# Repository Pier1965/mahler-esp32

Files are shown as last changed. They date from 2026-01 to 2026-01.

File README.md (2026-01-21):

ESP 32 LOGGER FOR MAHLER CALORIMETER
-------------------------------------
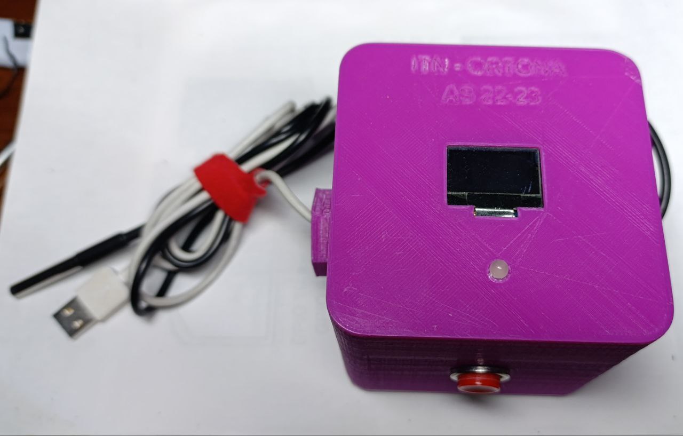
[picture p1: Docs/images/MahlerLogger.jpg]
Mahler temperature logger

CONFIGURAZIONE
---------------
I file da modificare prima della compilazione sono:
1. `include/config/define.h` per compilazione condizionale;
2. `include/config/hw_settings.h` per pin e parametri riguardanti l'hw;
3. `include/config/mail_settings.h` per i parametri SMTP del provider di posta elettronica;
4. `include/config/ntp_settings.h` eventuale cambio del server ntp, ora locale e ora legale;
5. `include/config/parametri_prova.h` contiene il numero massimo di misure da fare e il tempo tra le stesse in millisecondi;
6. `src/globals/global_variables.cpp` la mail del ricevente di default, che può anche essere cambiata
a run time dal portale MahlerAP;

USO
-----
1. Attivare l'ESP32;
    - Se la rete non è configurata, connettersi a "MahlerAP" con un cellulare o altro;
    - Se si vuole cambiare la rete cui si connette ESP, in modalità OZIOSO schiacciare per 10s il pulsante
(led color bianco. e connettersi a "MahlerAP" con un cellulare o altro;
2. Con il browser andare all'indirizzo 192.168.4.1 e immettere i dati della rete cui connettere l'ESP;
3. L'ESP si riavvierà e si collegherà in automatico alla rete configurata;
4. L'ESP entrerà in modalità OZIOSA col led verde lampeggiante;
5. Iniziare la prova schiacciando il pulsante per 0.5s circa. Il led diventerà rosso;
6. Se si vuole interrompere in anticipo il test, schiacciare il pulsante per circa 2s;
7. Al termine della prova il led diventa viola, viene inviata la mail con il file delle letture;
8. Il led torna verde lampeggiante e può essere eseguita una nuova prova.

********************************************************************************************************
CONFIGURATION
-------------
The files to modify before compilation are:

1. `include/config/define.h` for conditional compilation;
2. `include/config/hw_settings.h` for pins and parameters related to hardware;
3. `include/config/mail_settings.h` for SMTP parameters of the email provider;
4. `include/config/ntp_settings.h` for possible changes to the NTP server, local time, and daylight saving time;
5. `include/config/parametri_prova.h` contains the maximum number of measurements to take and the time between them in milliseconds;
6. `src/globals/global_variables.cpp` the default recipient email, which can also be changed at runtime from the MahlerAP portal;

USE
---
1. Turn on the ESP32;
    - If the network is not configured, connect to "MahlerAP" with a phone or other device;
    - To change the network the ESP connects to, in OZIOSO mode press the button for 10 seconds (white LED. and connect to "MahlerAP" with a phone or other device;
2. Using a browser, go to address 192.168.4.1 and enter the credentials for the network to connect the ESP to;
3. The ESP will reboot and automatically connect to the configured network;
4. The ESP will enter OZIOSO mode with a blinking green LED;
5. Start the test by pressing the button for approximately 0.5 seconds. The LED will turn red;
6. To interrupt the test early, press the button for approximately 2 seconds;
7. At the end of the test, the LED turns purple, and the email with the readings file is sent;
8. The LED returns to blinking green, and a new test can be performed.

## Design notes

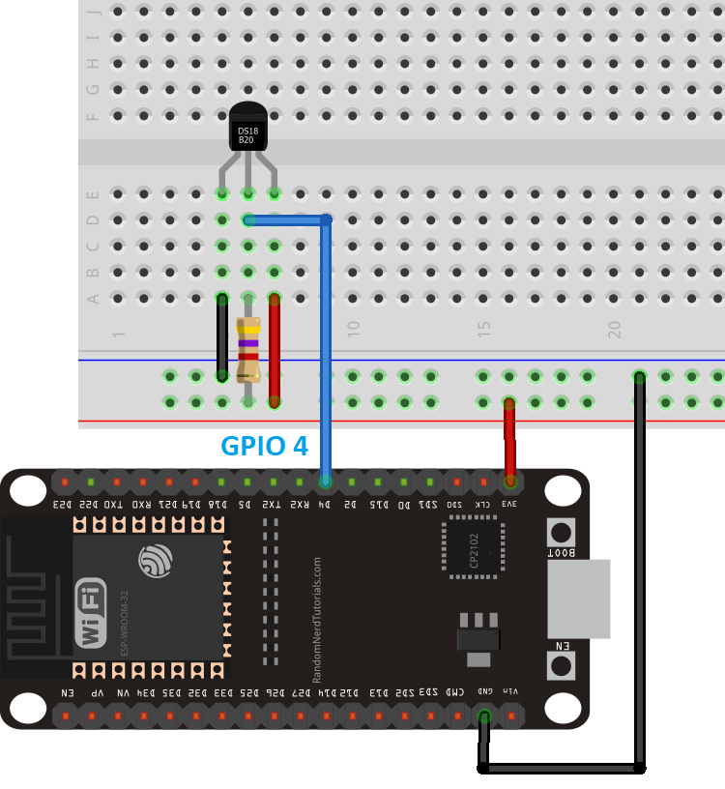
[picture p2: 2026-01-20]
Docs/schematic/ds18b20_esp32_single_normal.webp

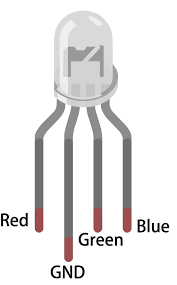
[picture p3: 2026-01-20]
Docs/schematic/rgb_cc.png

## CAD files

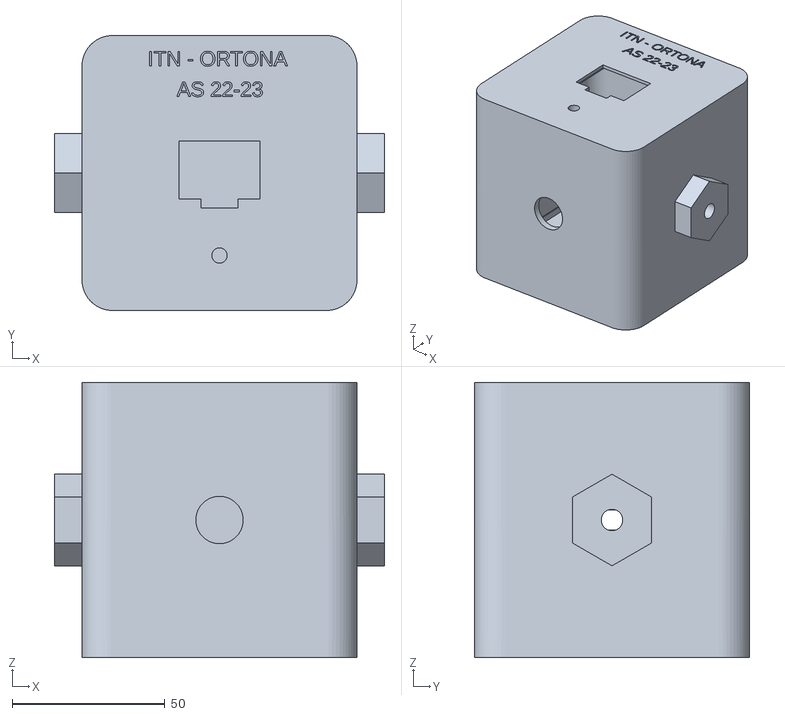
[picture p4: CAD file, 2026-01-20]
Docs/Mahler-drawings/Assembly.stl
108.0 x 90.0 x 90.0

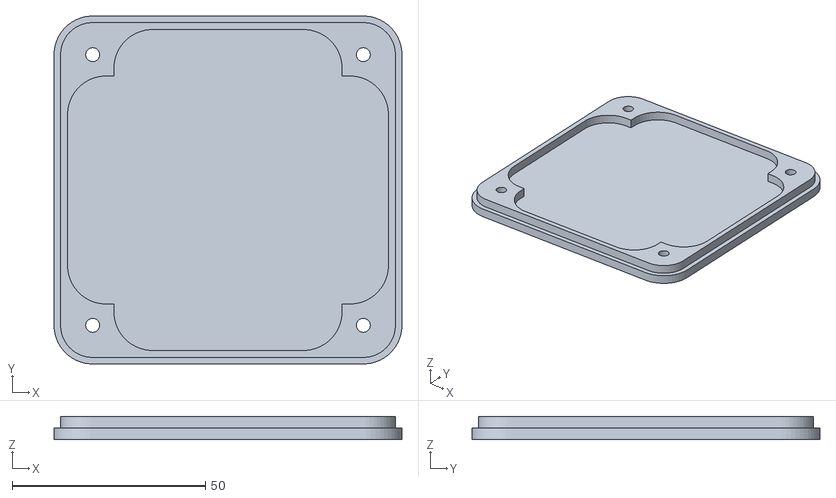
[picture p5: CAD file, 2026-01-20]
Docs/Mahler-drawings/tappo-case.stl
90.0 x 90.0 x 6.00

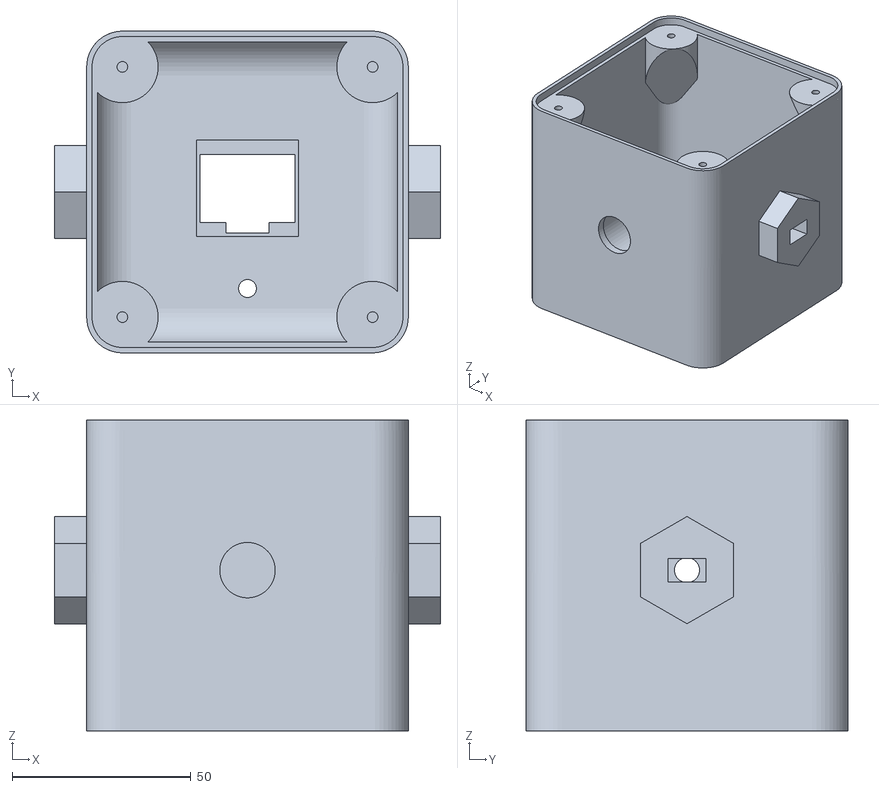
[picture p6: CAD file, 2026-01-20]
Docs/Mahler-drawings/case.stl
108.0 x 90.0 x 87.0

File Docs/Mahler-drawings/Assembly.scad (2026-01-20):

include <case.scad>
include<tappo-case.scad>

// Case 
color("blue",1)
    translate([L,0,L])
        rotate([0,180,0])
            case();
 // Tappo
 color("yellow",1)
    tappocase();

 
 
 
 


 

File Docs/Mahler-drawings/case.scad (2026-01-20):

include <dimensioni.h>
include <moduli.h>
/************************************/
module case(){
union(){
    difference(){
       union(){
        //La scatola è alta L meno il tappo S
        //Pieno
        translate([rr,rr,0]){
            linear_extrude(L-S){
                minkowski(){
                    square(L-2*rr,false);
                    circle(rr);
                };
            };
        }
        //baionette allineamento e passaggio cavi
        translate([-3*S,L/2,L/2])
            rotate([0,90,0])
                cylinder($fn=6,L+2*3*S,D/2,D/2);
        }
        //Sottraggo per svuotare
        translate([rr,rr,S]){
            linear_extrude(L-S){
                minkowski(){
                    square(L-2*rr,false);
                    circle(rr-S);
                };
            };   
        }
        //Sottraggo il dentino superiore per 
        //inserire metà spessore del tappo chiusura
        //spesso 2S
        translate([rr,rr,L-S-S]){
            linear_extrude(3){
                minkowski(){
                    square(L-2*rr,false);
                    circle((rr+rr-S)/2);
                 };
            };
        };
        
        //sottraggo i foro passaggio spinetta sonta T
        translate([0,L/2,L/2])
            rotate([0,90,0])
                cylinder(8*S,Df/2,Df/2,true);
        
        translate([L-4*S,L/2,L/2])
        rotate([90,0,0])
        rotate([0,90,0])
        linear_extrude(8*S)
        square([Busb,Husb],true);
            
        /*
       //sottraggo l'anello per inserimento forchetta sx di fissaggio
        translate([-2*S,L/2,L/2])
            rotate([0,90,0])
                difference(){
                    cylinder(S,2.5*D/2,2.5*D/2);
                     cylinder(S,A/2,A/2);
        }
         //sottraggo l'anello per inserimento forchetta dx di fissaggio
        translate([L+S,L/2,L/2])
            rotate([0,90,0])
                difference(){
                    cylinder(S,2.5*D/2,2.5*D/2);
                     cylinder(S,A/2,A/2);
        }
        */
        //Sottraggo la finestrella dell'OLED
        translate([colx,coly-dcoly,-1]){
            linear_extrude(5){
                square([Wo,Ho],true);
            translate([0,-ho/2-Ho/2,0])
                square([wo,ho],true);
            }
        }
        //Dentino OLED
        translate([colx,coly-dcoly,1.5]){
            linear_extrude(5){
                square([Wo+2,Ho+8],true);
            translate([0,-ho/2-Ho/2,0])
                square([wo,ho],true);
            }
        }
         // Foro passaggio LED
        translate([L/2,L/5,0]) 
            cylinder(10,dl/2,dl/2,true); 
        // Foro passaggio pulsante gestione
        translate([0,0,L/2]) 
            rotate([90,0,0])
                translate([L/2,0,0]) 
                    cylinder(10,dp/2,dp/2,true); 
        /*
         // Fori passaggio pulsanti
        translate([L/4,L*3/4,0])
            cylinder(10,dp/2,dp/2,true);   
         translate([L*3/4,L*3/4,0])
            cylinder(10,dp/2,dp/2,true);   
        translate([L/4,L/4,0])
            cylinder(10,dp/2,dp/2,true);   
         translate([L*3/4,L/4,0])
            cylinder(10,dp/2,dp/2,true);  
        //Foro di passaggio sensore IR
        translate([L/2-wir/2,L-S-S/2,L/4-hir/2])
            linear_extrude(2*S)
                square([wir,hir]);
        */
         //Testo da incidere
        translate([L/2+L/4+1,L-10,1])
            rotate([0,0,180])
                rotate([180,0,0])
                    linear_extrude(2)
                        text( "ITN - ORTONA", size= 5);
         translate([L/2+14,L-20,1])
            rotate([0,0,180])
                rotate([180,0,0])
                    linear_extrude(2)
                        text( "AS 22-23", size= 5);               
    };
    //Raccordi di rinforzo base
    translate([S,1.5*rr+(L-3*rr),S])
    rotate([90,0,0])
    raccordo(rr,L-3*rr);

    translate([1.5*rr,S,S])
    rotate([90,0,90])
    raccordo(rr,L-3*rr);

    translate([S+L-2*S,1.5*rr,S])
    rotate([90,0,180])
    raccordo(rr,L-3*rr);

    translate([L-3*rr+1.5*rr,S+L-2*S,S])
    rotate([90,0,-90])
    raccordo(rr,L-3*rr);

    //Rinforzi per viti chiusura tappo
    translate([rr,rr,L-S-S])
        rotate([180,0,-45])
            insertovite(rr,3*rr);

    translate([rr,rr+L-2*rr,L-S-S])
        rotate([180,0,-135])
            insertovite(rr,3*rr);

    translate([rr+L-2*rr,rr+L-2*rr,L-S-S])
        rotate([180,0,-45+180])
            insertovite(rr,3*rr);

    translate([rr+L-2*rr,rr,L-S-S])
        rotate([180,0,-45+180-90])
            insertovite(rr,3*rr);
}
}
       
//case();

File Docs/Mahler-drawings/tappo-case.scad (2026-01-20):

include <dimensioni.h>
module tappocase(){
    difference(){
    union(){
         //bordo usb
        //translate([xusbhole,yusbhole,0.01])
            //linear_extrude(1.8*S)
                //square([wusbhole+sbusb,husbhole+sbusb],true);
difference(){
union(){
 translate([rr,rr,0]){
            linear_extrude(S){
                minkowski(){
                    square(L-2*rr,false);
                    circle(rr);
                }
            }
        }
        
         translate([rr,rr,S]){
            linear_extrude(S){
                minkowski(){
                    square(L-2*(rr),false);
                    circle(rr-S/2-0.2);
                }
            }
        }
    }
    //Alleggerimento
    lall=L-2*rr-2*S-1;
    wall=L-2*rr-2*S-25;
     translate([L/2-wall/2,L/2-lall/2,S]){
            linear_extrude(S+0.1){
                minkowski(){
                    square([wall,lall],false);
                    circle(rr);
                }
            }
        }
        translate([L/2-lall/2,L/2-wall/2,S]){
            linear_extrude(S+0.1){
                minkowski(){
                    square([lall,wall],false);
                    circle(rr);
                }
            }
        }
    // Fori per viti
        rv=1.8;
    translate([rr,rr,-S/2])
    linear_extrude(3*S)
    circle(rv);
    translate([rr,L-rr,-S/2])
    linear_extrude(3*S)
    circle(rv);
    translate([L-rr,rr,-S/2])
    linear_extrude(3*S)
    circle(rv);
    translate([L-rr,L-rr,-S/2])
    linear_extrude(3*S)
    circle(rv);
     //Scassi teste
        rsc=3.5;
        psc=2.7;
        translate([rr,rr,-0.1])
    linear_extrude(psc)
    circle(rsc);
    translate([rr,L-rr,-0.1])
    linear_extrude(psc)
    circle(rsc);
    translate([L-rr,rr,-0.1])
    linear_extrude(psc)
    circle(rsc);
    translate([L-rr,L-rr,-0.1])
    linear_extrude(psc)
    circle(rsc);
}
}
}
}
//tappocase();

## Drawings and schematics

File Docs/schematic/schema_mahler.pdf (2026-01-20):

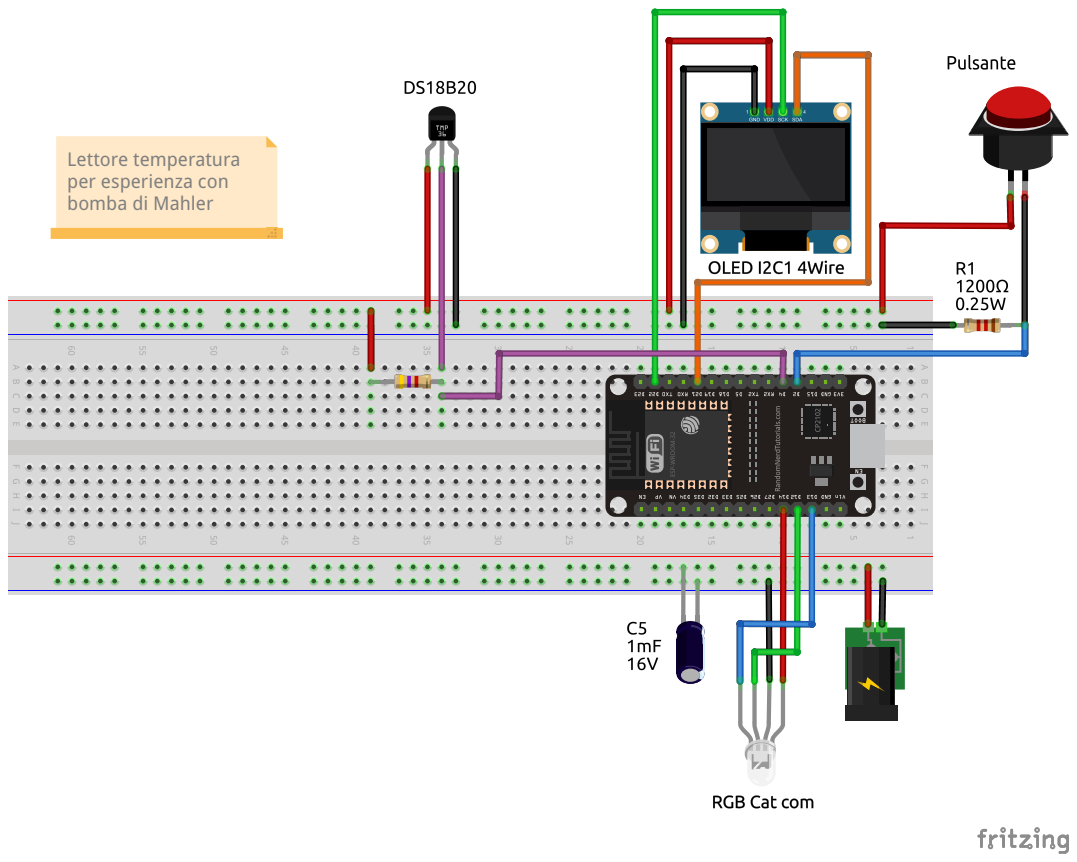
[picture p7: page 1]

Lettore temperatura
per esperienza con
bomba di Mahler

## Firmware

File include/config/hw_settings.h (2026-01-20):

#pragma once
//
// Schermo OLED
//
/*
  ---------------------------
  | JMDO 96C-1 OLED | ESP32 |
  ---------------------------
  | SDA             | 21    |
  | SCL             | 22    |
  | GND             | GND   |
  | 5V              | 5V    |
  ---------------------------
  pin già definiti nel core  -> wire begin funziona senza parametri
*/
constexpr int SCREEN_WIDTH = 128; // OLED display width, in pixels
constexpr int SCREEN_HEIGHT = 64; // OLED display height, in pixels
constexpr int HL = 8;             // altezza riga singola 
// Declaration for an SSD1306 display connected to I2C (SDA, SCL pins)
// The pins for I2C are defined by the Wire-library.
// On an arduino UNO:       A4(SDA), A5(SCL)
// On an arduino MEGA 2560: 20(SDA), 21(SCL)
// On an arduino LEONARDO:   2(SDA),  3(SCL), ...
// Esp32:   SDA -> G21, SCL -> G22 (sono di default in Arduino.h)
// comunque conviene definirli esplicitamente ed eventualmente usare dopo
// Wire.begin(I2C_SDA, I2C_SCL);
constexpr uint8_t I2C_SDA = 21;
constexpr uint8_t I2C_SCL = 22;
constexpr int OLED_RESET = -1; // Reset pin # (or -1 if sharing Arduino reset pin)
constexpr uint8_t SCREEN_ADDRESS = 0x3C; ///< See datasheet for Address; 0x3C for 128x64
/*
  ----------------------------
  | Pulsanti         | ESP32  |
  ----------------------------
  | Pulsante         | D02    |
  ----------------------------
*/
// pin cui è collegato il pulsante
constexpr int TRIGGER_PIN = 2;
// tempi di pressione del pulsante
constexpr unsigned long VERY_SHORT_PRESS_TIME = 50;    // debump filtro
constexpr unsigned long SHORT_PRESS_TIME = 1000;       // 1000 milliseconds
constexpr unsigned long LONG_PRESS_TIME = 5000;        // 5000 milliseconds
//
// Sensore di temperatura
//
// Precisione
//
constexpr int TEMPERATURE_PRECISION = 12;  	// higher resolution 12 bit -> 2^12 = 4092 valori
									// (125°C-(-55°C))/4096 = 0.0625°C
// pin Sensore di temperature
// GPIO where the DS18B20 is connected to
constexpr int oneWireBus = 4;
//
// Pin del led RGB
//
// Gestione RGB led catodo comune
//      R   C   G   B
// GPIO 14  Gr  12  13
//
// i pin 12, 13 e 14 danno interferenza con altri bus se in pwm
constexpr int redPin = 14; 		//25 -> migliore dei  12, 13, 14 
constexpr int greenPin = 12; 	// 26
constexpr int bluePin = 13; 	// 27

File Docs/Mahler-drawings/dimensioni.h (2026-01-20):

///////////////// Forma cubica principale ////////////////////////////
// Lato del cubo
L=90;
HC=150;
//Spessore pareti
S=3;
// Raggio di raccordo
rr=10;
//Accuratezza cilindri
$fn=50;
//Foro passaggio cavi
//Circoscrive esagono $fn=6
D=L/3;
//Foro passaggio cavo sonda temperatura
Rf=3.5;
Df=2*Rf;
//Foro rettangolare passaggio spinetta USB
Busb=10.5;
Husb=6.5;
//gioco per compensare il ritiro su foro esagonale
dRf=0.25;
//Oled
colx=L/2;
coly=L/2+1;
dcoly=0;
Wo=26.5;
wo=12;
Ho=19;
ho=3;
// Perno volume
dpv=7;
//Sensore IR
wir=7+0.5;
hir=5+0.5;
// Pulsanti
dp=15.5;
//LED
dl=5;
/////////////////// foro casse ///////////////////////////////
//Altoparlante
Ralt=50.5/2;
//ripresa ritiro
dRalt=0.1;
//Dentino appoggio altoparlante
ddRalt=1.25;
//////////////// Anello cass fissaggio retina ////////////////
Ha=3;
Rea=65/2;
Ria=Ralt-2;
Rffa=Ralt+3;
// Scasso vite
Rsv=3;
Hsv=3;
// Raggio foro fissaggio anello altoparlante vite M3
rffaa=1.5;
//////////////// Forchetta di arresto cubi ///////////////////
//Forchetta blocco casse
A=2*Rf+3;
//gioco su larghezza forchette
//per compensare il ritiro
dA=0.4;
//gioco spessore forchetta
dS=-0.3;
thf=S+dS;
dentey=4;
dentez=2*S;
//larghezza forchette laterali
lf=5;
//ingombro
wf=D+2*lf;
hf=L/2-2*S+D/2;
// Foro passaggio USB in tappo posteriore case
wusbhole=8.5;
husbhole=3.5;
xusbhole=L/2;
yusbhole=S+33+husbhole/2;
//bordino foro
sbusb=3;
///////////////////////// ESP 32 /////////////////////////////
//ESP32 Wroom
//Basetta
//pin
passo=2.54;
//dimensioni basetta wroom
w=11*passo;
l=22*passo;
th=1.5;
//Numero dei pin
npl=19;
//Numero file pin  distanza tra le file
dpw=10*passo;
npw=2;
// Fori di fissaggio
rf=1.25;
dfl=51;
dfw=23.5;
//cpu
wcpu=16;
lcpu=18;
thcpu=3;
xcpu=l-8-lcpu;
ycpu=w/2-wcpu/2;
//usb
wusb=7.4;
thusb=2.5;
lusb=5.8;
// pin a sezione quadrata
wpin=0.5;
lpin1=3;
lpin2=5.5;
lpin=11;
ypin=(w-10*passo)/2;
xpin=(l-18*passo)/2;
dwpin=10*passo;//(w-2*ypin);
//basepin
hbp=2.5;
rbp=passo/2;
/////////////////// basetta millefori ////////////////
//dimensioni basetta
wmf=(16+1)*passo;
//lmf=L-S-S-S;
lmf=23*passo;
//spessore millefori
smf=1.5;
//numero fori
nfy=lmf/passo;
nfx=wmf/passo;
//raggio foro pin
rfmf=sqrt(2*(wpin/2)^2);
//Dupont
hdup=8.5;

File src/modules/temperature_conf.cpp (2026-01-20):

#include "project.h"
#include "modules/temperature_conf.h"
#include "FS.h"
#include <LittleFS.h>
//
void start_sensor(){
  // Start the DS18B20 sensor
  oneWire.reset();
  delay(10);
  sensors.begin();
  delay(1000);
  //sensors.begin();
  //delay(100);
  int sensorCount = sensors.getDeviceCount();
  DEBUG_PRINT("Sensori rilevati: ");
  DEBUG_PRINTLN(sensorCount);
  delay(100);
  sensors.getAddress(tempDeviceAddress, 0);
  if (sensors.isConnected(tempDeviceAddress)) {
  		DEBUG_PRINTLN("DS18B20 trovato");
  		printSCR_MSG("DS18B20 Ok");
  		delay(1000);
  		// set the resolution to TEMPERATURE_PRECISION bit (Each Dallas/Maxim device is capable of several different resolutions)
        sensors.setResolution(tempDeviceAddress, TEMPERATURE_PRECISION);
        DEBUG_PRINT("Risoluzione bit: ");
        DEBUG_PRINTLN(TEMPERATURE_PRECISION);
        printSCR_MSG("DS18B20 res: 12bit");
        delay(1000);
    } else {
    	DEBUG_PRINTLN("DS18B20 non trovato!");
        printSCR_MSG("DS18B20 NOT connected!");
        for(;;); // Don't proceed, loop forever
    } 
  //sensors.setResolution(tempDeviceAddress, TEMPERATURE_PRECISION);
}
//
void get_temperature(int i){
  sensors.requestTemperatures(); 
  T[i]=sensors.getTempCByIndex(0);
}
//
void writeTempToFile(){
  DEBUG_PRINTLN("Scrittura dati su file"); 
  File file_temperature = LittleFS.open("/fileDati.txt", FILE_WRITE);
  String textMsg = String("Inizio ") + MESSAGGIO + Data + " alle " + Ora + "\n";
  file_temperature.print(textMsg);
  for (int n = 0; n < N_SAMP_DONE; n++) {
    float temp = float(n)*float(DT_SAMPLINGS)/1000;
    file_temperature.print(temp);
    file_temperature.print(" ");
    file_temperature.println(T[n]);
  }
  getTime();
  textMsg.clear();
  textMsg = String("Fine ") + MESSAGGIO + Data + " alle " + Ora + "\n";
  file_temperature.print(textMsg);
  file_temperature.close();
  display.clearDisplay();
  display.println("Verifica fileDati.txt");
  delay(2000);
  DEBUG_PRINTLN("Lettura dati su file"); 
  file_temperature = LittleFS.open("/fileDati.txt");
  if(!file_temperature){
    DEBUG_PRINTLN("There was an error opening the file for reading");
    display.clearDisplay();
    display.println("No fileDati.txt");
    delay(2000);
    return;
  }else{
    file_temperature.close();
    DEBUG_PRINTLN("Fatto...");
  }
}
//
void readTempToFile(){
  DEBUG_PRINTLN("Lettura dati su file"); 
  File file_temperature = LittleFS.open("/fileDati.txt");
  if(!file_temperature){
  DEBUG_PRINTLN("There was an error opening the file for reading");
return;
  }
  while(file_temperature.available()){
    Serial.write(file_temperature.read());
  }
  file_temperature.close();
  DEBUG_PRINTLN("Fatto...");
}
//
void do_test(){
  N_SAMP_DONE = 0;
  getTime();
  for (int i=0;((i<N_SAMPLINGS)&&(STATO == AppState::TESTING));i++){
    get_temperature(i);
    unsigned long t_init = millis();
    N_SAMP_DONE = i+1;
    DEBUG_PRINT(T[i]);
    DEBUG_PRINTLN("ºC");
    String str = String(i) + ":" + String(T[i]) + "C";
    printSCR_lettura(str);
	for(;((millis() - t_init)<DT_SAMPLINGS);){
		chk_button();
		ledRGB.flash_led();
    }
    str="           ";
    printSCR_lettura(str);
  }
  DEBUG_PRINTLN("------------------------");
  for(int i=0;i<N_SAMP_DONE;i++){
    DEBUG_PRINT(T[i]);
    DEBUG_PRINTLN("ºC");
  }
  writeTempToFile();
}
//
void print_temperatura_SCR(){
  get_temperature(0);
  String str = "T:" + String(T[0]) + "C";
  printSCR_lettura(str);
}
